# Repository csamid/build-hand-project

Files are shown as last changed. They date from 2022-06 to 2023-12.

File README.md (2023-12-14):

# CSULB BUILD Hand Project

As an CSULB NIH BUILD Scholar I worked in the Robotics and Interactive Systems Engineering laboratory on a hand rehabilitation project. This project was co-advised by Dr. Panadda Marayong and Dr. I-Hung Khoo (many thanks to them!). The goal of our project was to measure hand forces and torques for evaluation and rehabilitative training of individuals with hand impairment. Our project consists of a knob device and a grip-load device to simulate interactions that involve power and precision. Below you can find more details on each device and some other work I did.

> [!NOTE]
> This repo is primary for future csulb students that will build ontop of the work I and many previous students developed. However anyone can view/use the material. Feel free to contact me if you have any questions!

## Contents
- [Grip Load Device](#grip-load-device)
- [Brace](#bracee)
- [Knob Device](#knob-device)
- [Hapkit](#hapkit)

## GRIP LOAD DEVICE
The Grip-Load Device (GLD) runs on a Arduino Uno and incorporates data from three sensors:
- MPU6050 for acceleration to measure load force during dynamic tests. 
- LCFD-50 load cell to capture grip force 
- LSB302 Futek load cell to assess load force during static tests

The purpose of this device is to assess the differences in grip-load force coordination between healthy and hand impaired individuals. We also hope this device can provide rehabilitative training to individuals with hand impairment.

Dive deeper into the Grip Load Device:

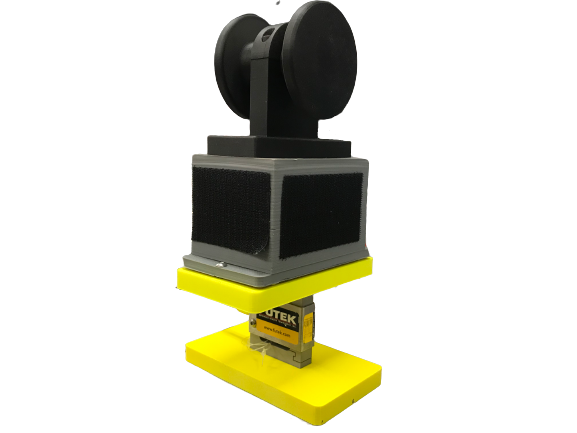
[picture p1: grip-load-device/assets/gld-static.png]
gld device


# Brace
A 2 piece 3d printed adjustable brace to explore the effects of wrist position on grip-load force coordination. It can be set at -30, 0, and 30 degrees at the wrist.

Head to the Brace directory: 

<div style="text-align: center; padding-bottom: 50px;">
<a href="brace/">
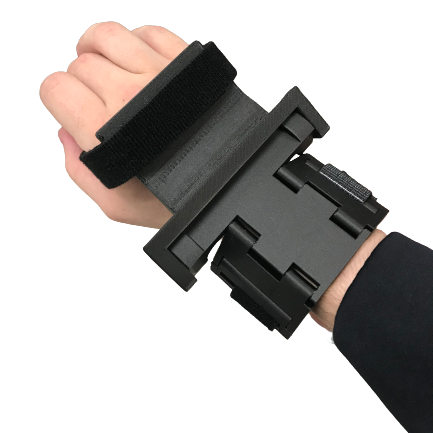
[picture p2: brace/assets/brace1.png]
brace
  
</a>
</div>

# Knob Device
The knob device centers around an Arduino Uno, sending data to a  graphical user interface (GUI) and controlling a haptic interface. This device aims to assess the coordination between grasping force and  turning torque. LabVIEW  handles the GUI and data acquisition. The haptic interface comprises a HEDS encoder, a maxon A-max motor, force sensing resistors  (FSR), and a torque sensor.

Dive deeper into the Knob Device:

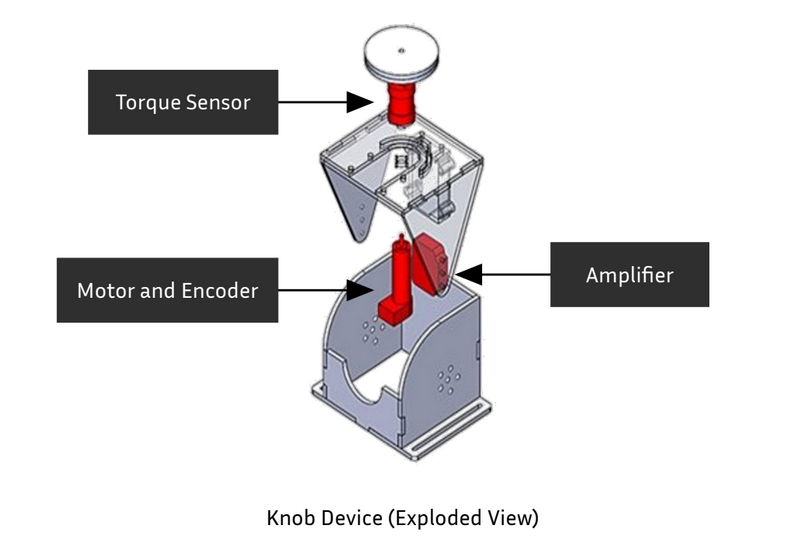
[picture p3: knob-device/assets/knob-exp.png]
Knob Device


# Hapkit
Some design changes were made to the open-source Hapkit 10.01.14 from Stanford to fit with available hardware at the RISE Lab @CSULB.

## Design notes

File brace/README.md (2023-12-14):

## Brace

Project Timeline: Feburary 2022 - May 2022

### Contents
- SolidWorks Files
- 3D printer Files
- References
- Bill of Materials

### Bill of Materials
| Category          | Product                  | Description          | Individual Quantity per Brace | Purchase Quantity | Price  |
| ----------------- | ------------------------ | -------------------- | ------------------------------ | ----------------- | ------ |
| Hardware          |                          |                      |                              |                   |       |
|                  | [Heat Threaded Inserts](https://www.mcmaster.com/94180a331/) | M3, 3.9 mm length         | 2                            | 1                  | $16.81 |
|                  | [Heat Threaded Inserts](https://www.mcmaster.com/94180A312/) | M2, 4.8 mm length         | 6                            | 1                  | $17.18 |
|                  | [Hex Socket Cap Screws](https://www.mcmaster.com/91292A833/)    | M2 10 mm length       | 6                            | 1                  | $7.91  |
|                  | [Socket Cap Screws](https://www.mcmaster.com/92855A310/)        | M3 10 mm length       | 2                            | 1                  | $2.50  |
| 3D Printed Parts  |                        |                      |                              |                   |       |
|                  | Palm (regular or large size)   | Printed in CSULB's Innovation Space (Markforged Printer, onyx material) | 1 | 1 | ~$5.00 |
|                  | Wrist (regular or large size)  | Printed in CSULB's Innovation Space (Markforged Printer, onyx material) | 1 | 1 | ~$5.00 |
| Other             |                        |                      |                              |                   |       |
|                  | [Velcro](https://www.amazon.com/gp/product/B00I0TTPL8/ref=ppx_yo_dt_b_search_asin_title?ie=UTF8&psc=1)                   | one-wrap strap 1"    | 1                            | 1                  | $6.50  |
| Total Cost        |                        |                      |                              |                   | $60.90 |

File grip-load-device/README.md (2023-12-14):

## Grip Load Device

Project Timeline (August 2021 - June 2022)

Check out my [presentation poster](assets/RSCA2022_Samid_Ceballos.pdf) to learn more!

#### For Students:
This repo contains the code, documentation, and parts for this device. The data collection is done on LabVIEW. Videos explaining how to download code, how arduino & LabVIEW code works, and how run the code can be found [here](https://www.youtube.com/playlist?list=PLc3eWZpUKAzyQBUwwpyzYRb3LxGoiJ5aO ).

### Bill of Materials
| Category    | Product                                       | Description                                    | Individual Quantity Needed |
| -----------  | -------------------------------------------- | ---------------------------------------------- | -------------------------- |
| Hardware    |                                              |                                                |                           |
|             | [Hex Socket Head Cap Screws](https://www.mcmaster.com/91251A346/)                    | 10-32, 7/8", Alloy Steel                      | 2                         |
|             | [Socket Head Screw](https://www.mcmaster.com/93615A380/)                             | 10-32, 1/2"                                  | 1                         |
|             | [Heat Threaded Inserts](https://www.mcmaster.com/93365A154/)                          | 10-32, 0.225"                                | 1                         |
| Electronics |                                              |                                                |                           |
|             | CSG110                                       | Strain gauge amplifier for the LSB302         | 1                         |
|             | LCFD-50                                      | Load Cell for Grip Force                      | 1                         |
|             | Futek LSB302                                 | Load Cell for Load Force                      | 1                         |
|             | MPU-6050                                    | 6-DOF Accl and Gyro sensor                    | 1                         |
|             | HX711                                       | Load Cell Amplifier                           | 1                         |
|             | Arduino Uno                                 | microcontroller                               | 1                         |
|             | PCB                                         | made in house by Dr. Khoo                    | 1                         |
| 3D Printed Parts |                                    |                                                |                           |
|                 | bottom_collar2                           | printed in CSULB's Innovation Space (Markforge Printer, onyx material)   | 1   |
|                 | plate_attachment                          | printed in CSULB's Innovation Space (Markforge Printer, onyx material)   | 2   |
|                 | top_collar2                              | printed in CSULB's Innovation Space (Markforge Printer, onyx material)   | 1   |
|                 | weightcomp                               | printed in CSULB's Innovation Space (Markforge Printer, onyx material)   | 1   |

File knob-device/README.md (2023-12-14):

## Knob Device

Project Timeline: June 2020 - May 2021

[Watch a presentation I gave to learn more!](https://www.youtube.com/watch?v=llJ-72yHejI)

#### For future students:
The code from this device has not been updated since mid 2021 so it can use some improvements. See the [Grip Load Device LabVIEW code](../grip-load-device/LabVIEW/) for improving the LabVIEW code. Improvements can be made on the arduino code to add/change the haptic environment (ex: Spring and Damper). Hardware/Sensor improvements are also welcome, since FSR's are not reliable quantitatively. 

My final work on this device was this 3D-printed snap lock for the torque sensor. This piece was never fully tested to support the torque we expect users to apply. Here would be a good place to start!

Snap Lock:

<a href="knob-device/">
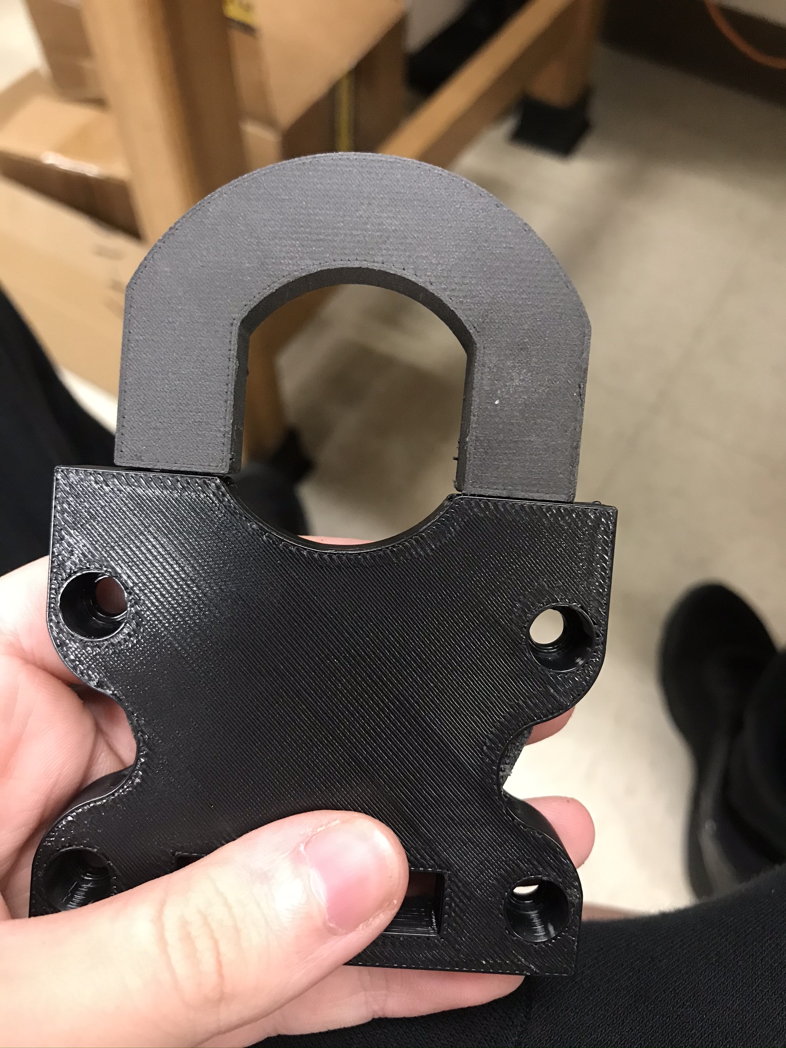
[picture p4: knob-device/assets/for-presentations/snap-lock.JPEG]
snap lock
  
</a>

Some notes on recorded max torque:

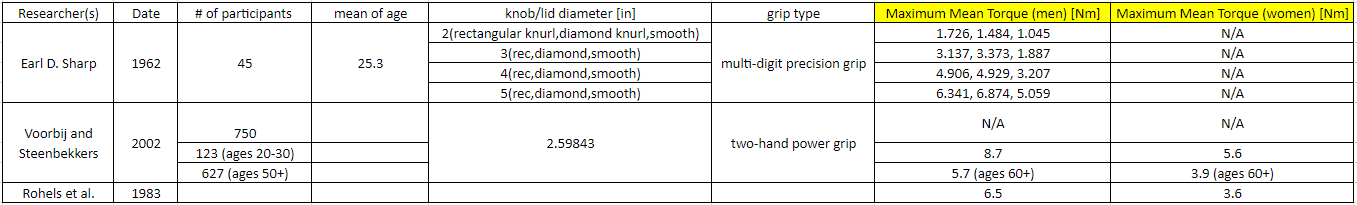
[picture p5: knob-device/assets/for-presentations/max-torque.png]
max-torque


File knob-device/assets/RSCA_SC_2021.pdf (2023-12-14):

# Hand Grasp Assessment Device with

# Variable Haptic Feedback– Work In

# Progress

# Samid Ceballos

1

, Panadda Marayong, Ph.D.
1

, and I-Hung Khoo, Ph.D.
2
[1] Department of Mechanical and Aerospace Engineering,

## [2] Department of Electrical Engineering

## Robotics and Interactive Systems Engineering (RISE) Laboratory

# Introduction

# Hand impairment is common in elderly over the age of 65 due

# to neuromuscular disorders and loss of skeletal muscle mass

[1]

# Previous robot-assistive devices can provide intensive hand

# rehabilitation which promotes neuroplasticity; however, these

# systems are costly[4,5]

# Previously, a low-cost device was developed to assess grip force

# vs load force and arm movement coordination

[3]

# Existing robot-assistive devices for turning tasks focus on

# turning torque[2,4] and grasping independently

[5,6]

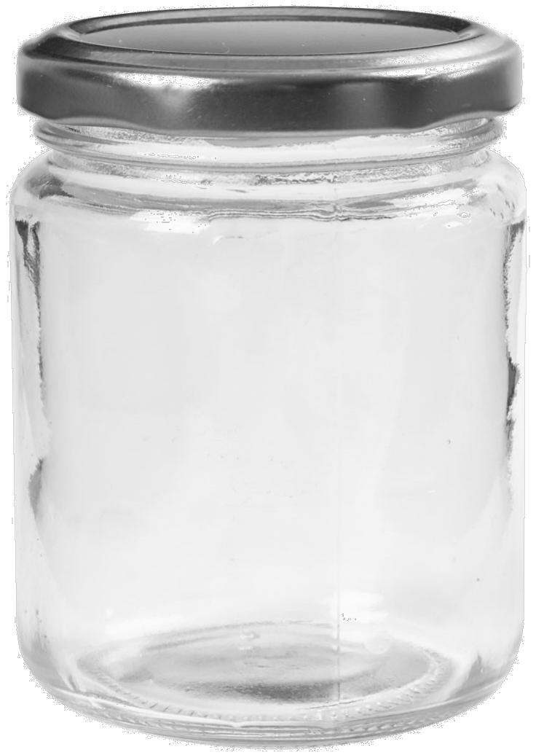
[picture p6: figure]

Figure 1. Jar

[7]

Hand Cup Body

Electronics
Chassis

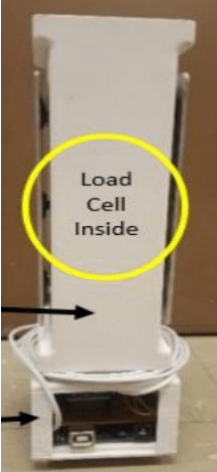
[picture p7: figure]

Figure 2. Grip/Load Device

# Acrylic structure with three available knob sizes

and five angles from the horizontal.

# DC motor with encoder for variable torque

# feedback and turn angle measurement

# Torque sensor to acquire turning torque

# Arduino Uno microcontroller with motor shield

# for sensor integration and actuation control

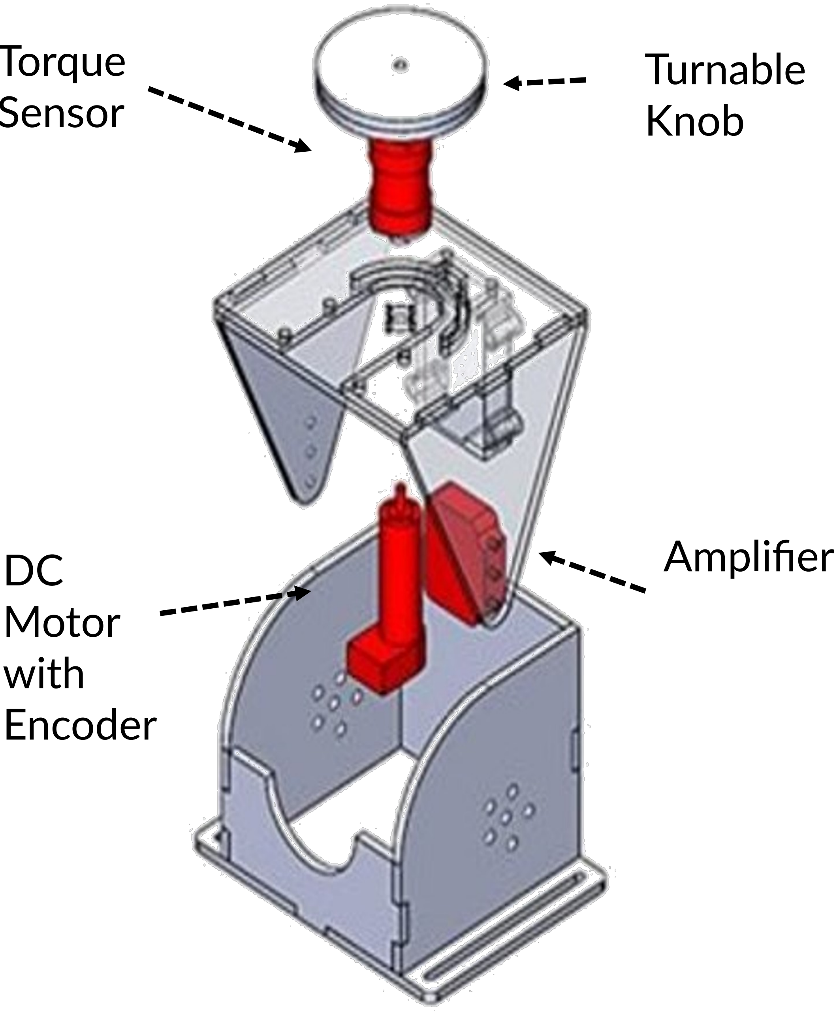
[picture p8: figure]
Amplifier; Motor; with; Encoder

Turnable
Knob

Torque
Sensor

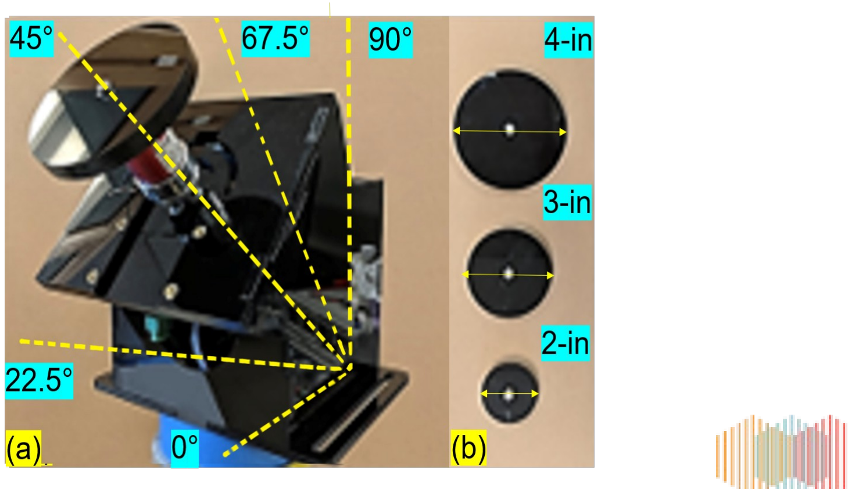
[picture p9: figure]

Figure 4. (a) Device at 45° plane from the horizontal (b) Available knob sizes

Figure 3. Exploded view

# Hand Device System Overview – Hardware Design

# Hand Device System Overview - Sensor Integration

# Force Sensing Resistor (FSR)

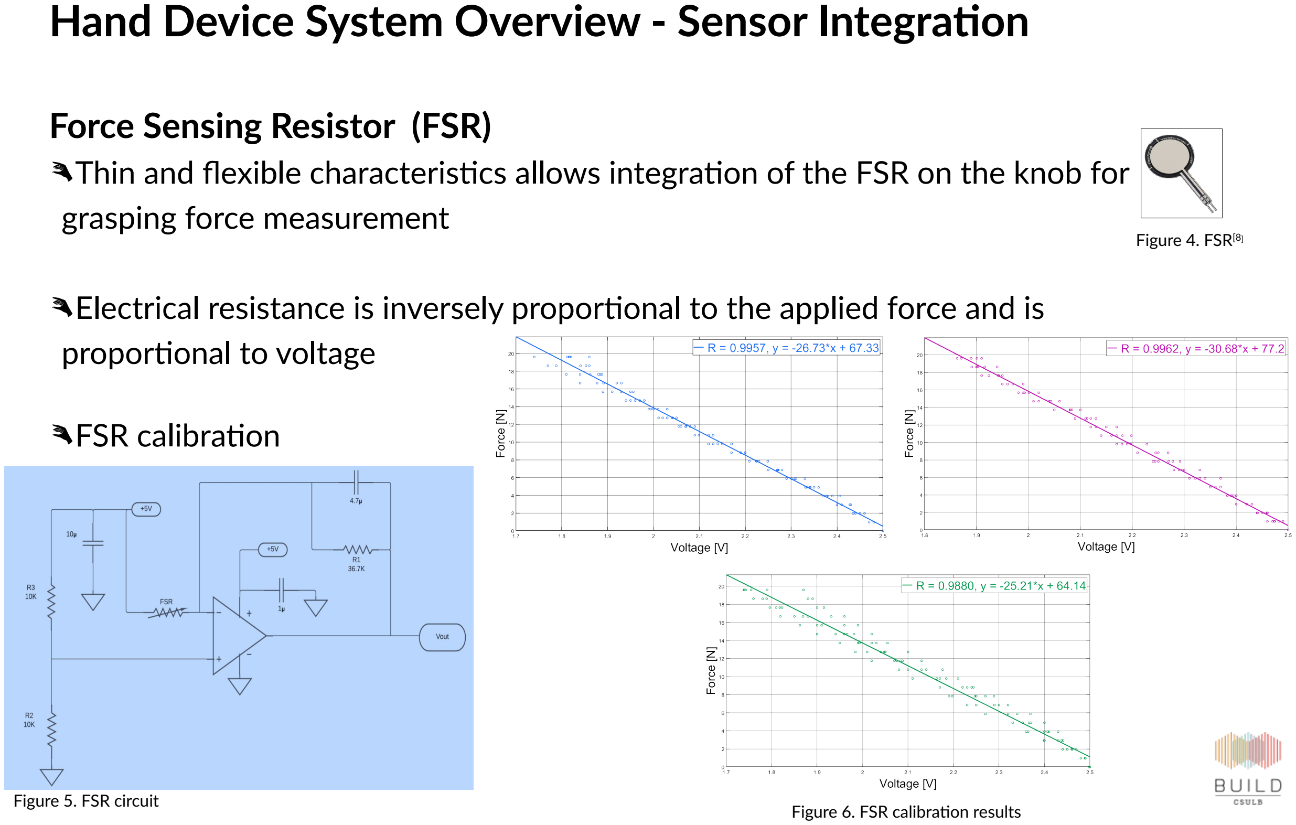
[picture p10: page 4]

# Thin and flexible characteristics allows integration of the FSR on the knob for

# grasping force measurement

# Electrical resistance is inversely proportional to the applied force and is

# proportional to voltage

# FSR calibration

Figure 4. FSR[8]

Figure 5. FSR circuit | Figure 6. FSR calibration results

# Hand Device System Overview - Sensor Integration

# Torque Sensor

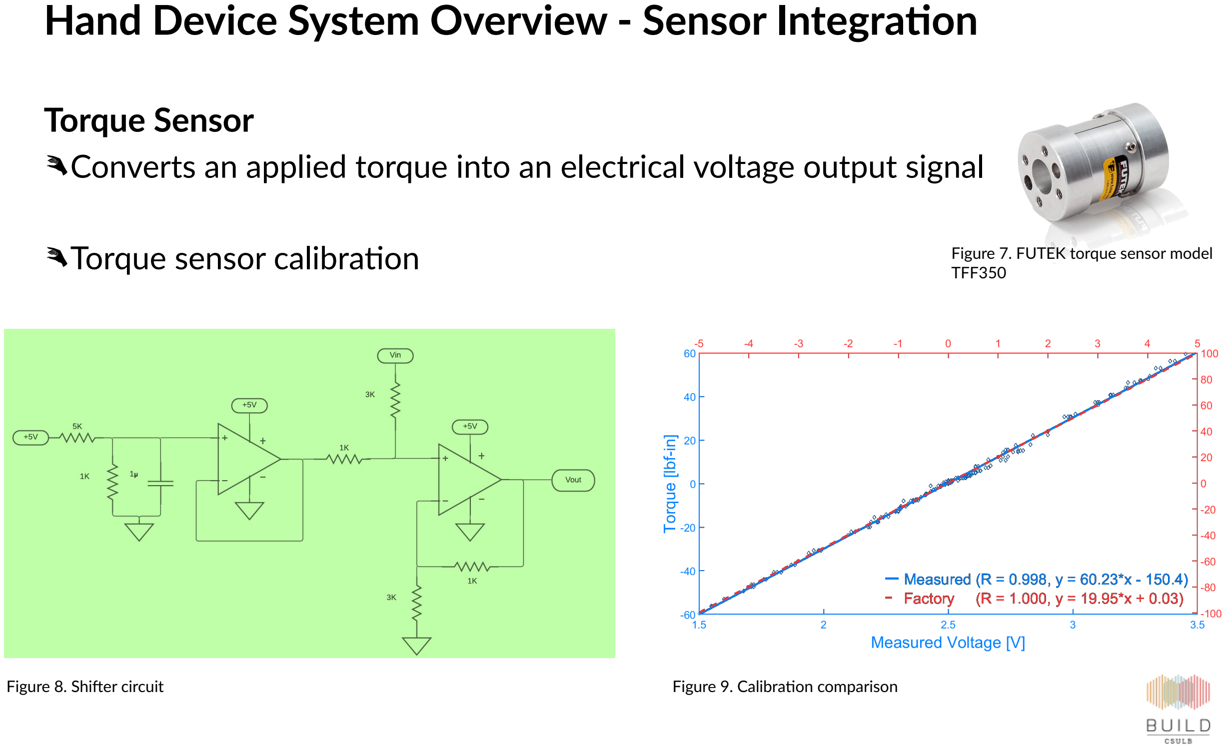
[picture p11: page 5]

# Converts an applied torque into an electrical voltage output signal

# Torque sensor calibration

Figure 8. Shifter circuit | Figure 9. Calibration comparison

Figure 7. FUTEK torque sensor model TFF350

# Hand Device System Overview –Graphical User Interface (GUI)

# Developed in LabVIEW to display experiment variables

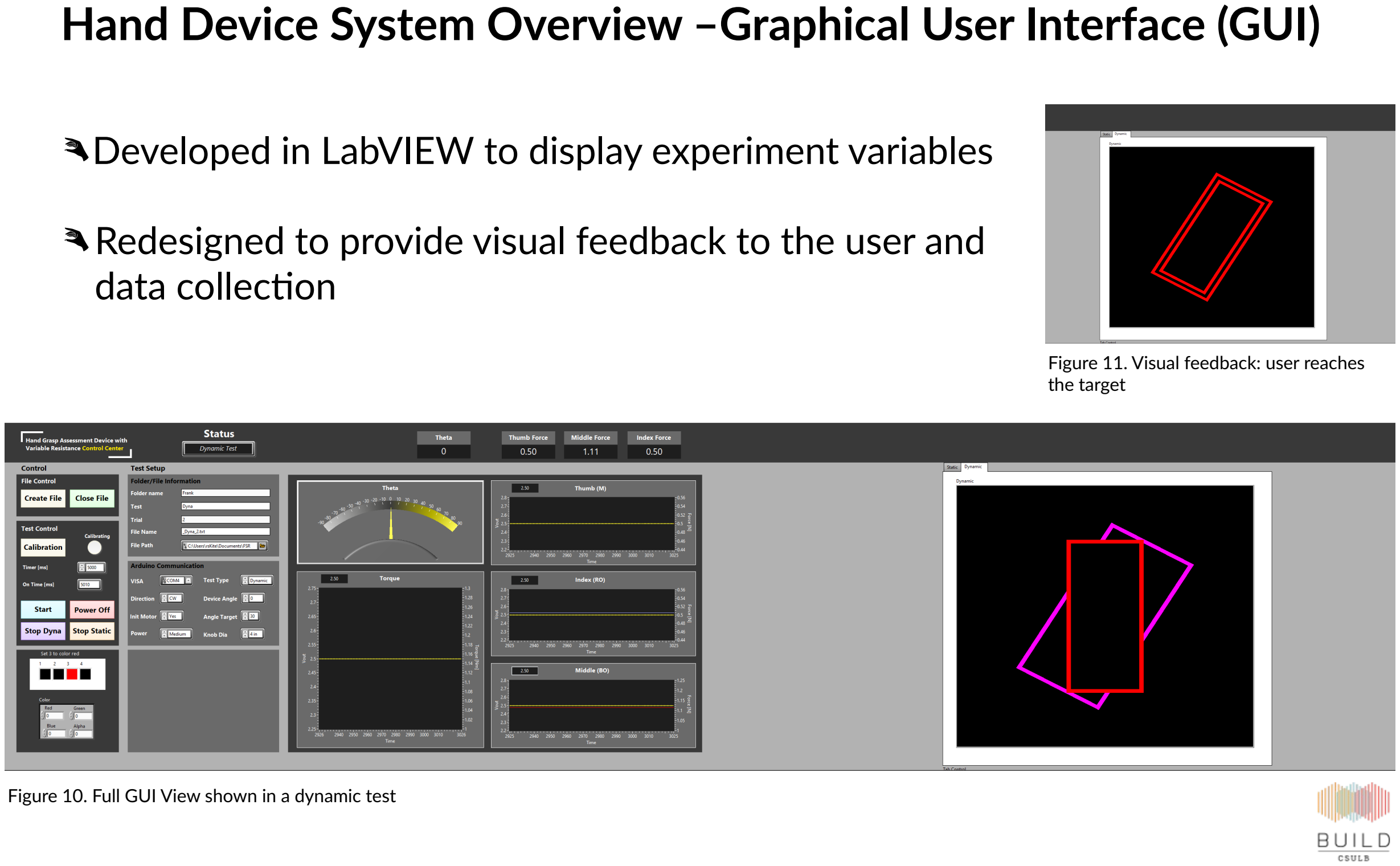
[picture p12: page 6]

Figure 10. Full GUI View shown in a dynamic test

Figure 11. Visual feedback: user reaches the target

# Redesigned to provide visual feedback to the user and

# data collection

# Hand Device System Overview

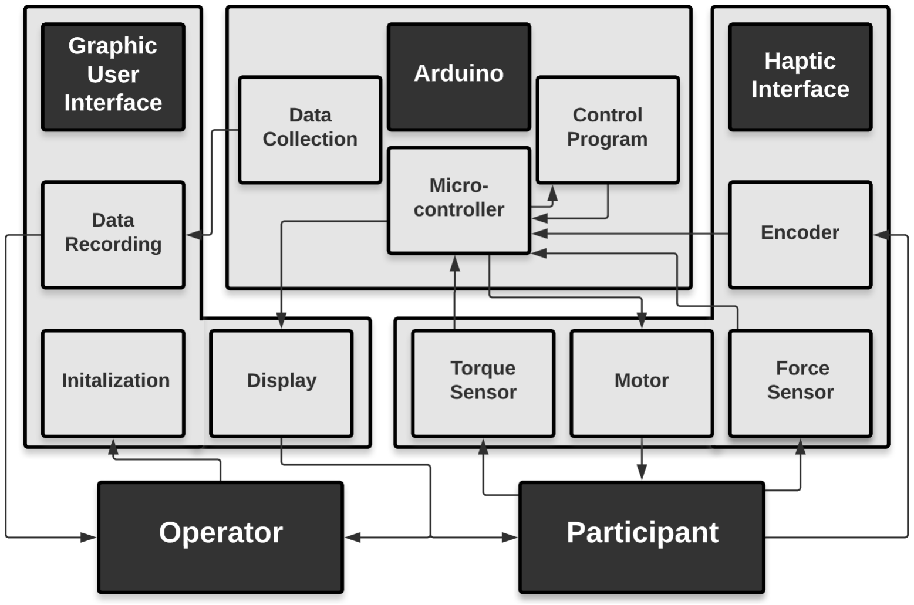
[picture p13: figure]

Figure 12. System design layout

# Human Subject Experiment Protocol

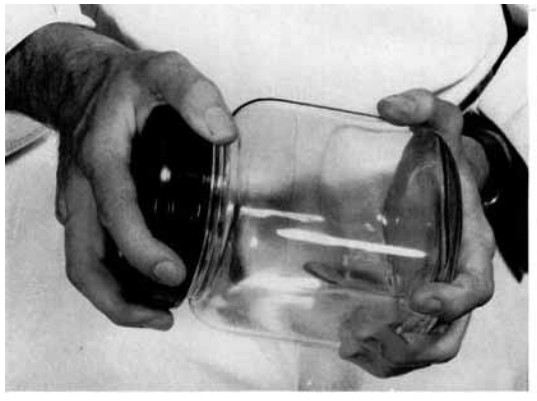
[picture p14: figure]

# Static Test (Power Focus)

# Max turning torque at varying knob sizes and wrist

# extension

# Dynamic Test (Precision Focus)

# Grasping force against turning torque at different

# resistance levels

# Target over- and undershoot of turn angle at varying

# torque feedback

# Time to target during target angle test

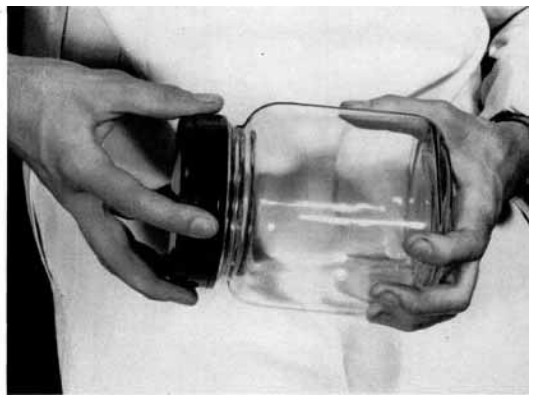
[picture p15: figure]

Figure 13. Transition of a power grasp (top) into a precision grasp (bottom) while opening a jar

[9]

# Future Work

# Redesign knobs for FSR integration and design attachment for static

# testing

# Test the functionality of the device with healthy subjects

# Baseline data collection for assessing coordination between

# grasping force and turning torque with healthy and hand impaired

# subjects

# Integration of a grip force/load force device that was previously

# developed for a more detailed hand evaluation

This research was supported by the National Institute of General Medical Sciences of the National Institutes of Health under Award Numbers; UL1GM118979; TL4GM118980; RL5GM118978. The content is solely the responsibility of the authors and does not necessarily represent the official views of the National Institutes of Health. The authors would like to thank Don G. Napasindayao for initial development of the device.

1.Carmeli, E., et al. “The Aging Hand.” The Journals of Gerontology: Series A, vol. 58, no. 2, 1 Feb. 2003, doi:10.1093/gerona/58.2.m146.

2.Gurari, N., and A. M. Okamura. “Human Performance in a Knob-Turning Task.” Second Joint EuroHaptics Conference and Symposium on Haptic

Interfaces for Virtual Environment and Teleoperator Systems (WHC'07), 2007, doi:10.1109/whc.2007.71

3.Herrera, D. "Hand Force and Arm Movement Coordination in Static and Dynamic Manipulation Tasks." California State University, Long Beach, 2018. [MS

Thesis]

4.Kazemi, H., et al. “A Robotic Interface to Train Grip Strength, Grip Coordination and Finger Extension Following Stroke.” 2012 Annual International Conference

of the IEEE Engineering in Medicine and Biology Society, 28 Aug. 2012, doi:10.1109/embc.2012.6346820.

5.Metzger, J., et al. “Design and Characterization of the ReHapticKnob, a Robot for Assessment and Therapy of Hand Function.” 2011

IEEE/RSJ International Conference on Intelligent Robots and Systems, 25 Sept. 2011, doi:10.1109/iros.2011.6094882.

6.Romeo, R.A, et al. "Development and preliminary testing of an instrumented object for force analysis during grasping," 2015 37th Annual Conference of the IEEE

Engineering in Medicine and Biology Society (EMBC), Milan, 2015, doi: 10.1109/EMBC.2015.7319935.

7.12 x Candle or Storage Jar. (n.d.). [Photograph]. Pastimes. https://www.google.com/url?sa=i&url=https%3A%2F%2Fwww.pastimesltd.co.uk%2F12-x-candle-or-

storage-jar-2698-p.asp&psig=AOvVaw3DwXC7F2fkro_Gv1-

1bnD1&ust=1615059864829000&source=images&cd=vfe&ved=0CAIQjRxqFwoTCODT4_30me8CFQAAAAAdAAAAABBW

8.FLEXIFORCE A401 SENSOR 25LBS. (n.d.). [Photograph]. Antratek Electronics. https://cdn.antratek.nl/media/product/8c2/flexiforce-a401-sensor-25lbs-sen-

11207-098.jpg

9.Napier, John R. "The prehensile movements of the human hand." The Journal of bone and joint surgery. British volume 38, no. 4 (1956): 902-913, doi:

10.1302/0301-620X.38B4.902.

# References & Acknowledgements

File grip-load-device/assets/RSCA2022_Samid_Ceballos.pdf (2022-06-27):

# A user interface for evaluating hand force coordination in static and dynamic

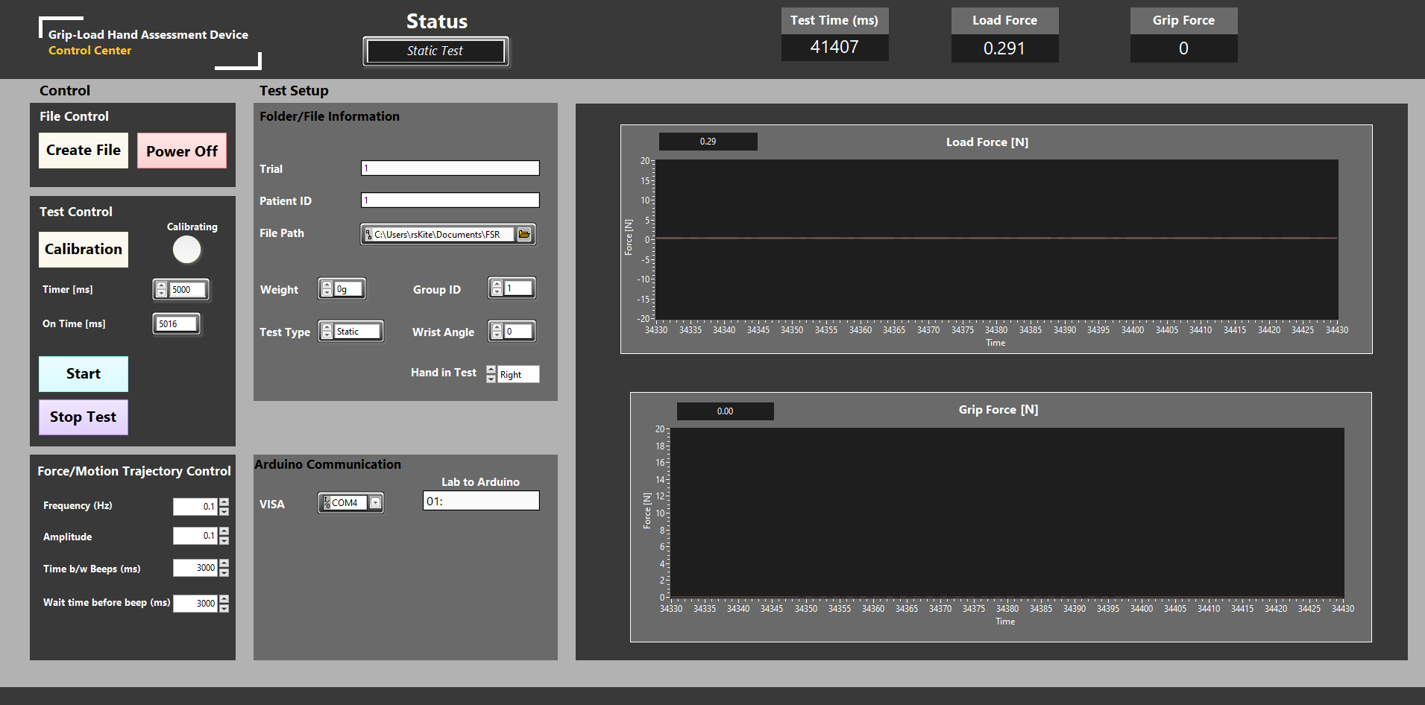
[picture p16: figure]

# manipulation tasks

## Samid Ceballos¹

## , Panadda Marayong, Ph.D.¹

, I-Hung Khoo, Ph.D.

2

## , and Vennila Krishnan, Ph.D., PT

3

## 1Department of Mechanical and Aerospace Engineering 2Department of Electrical Engineering 3Department of Physical Therapy

Haptic feedback

Visual feedback

Central Nervous System

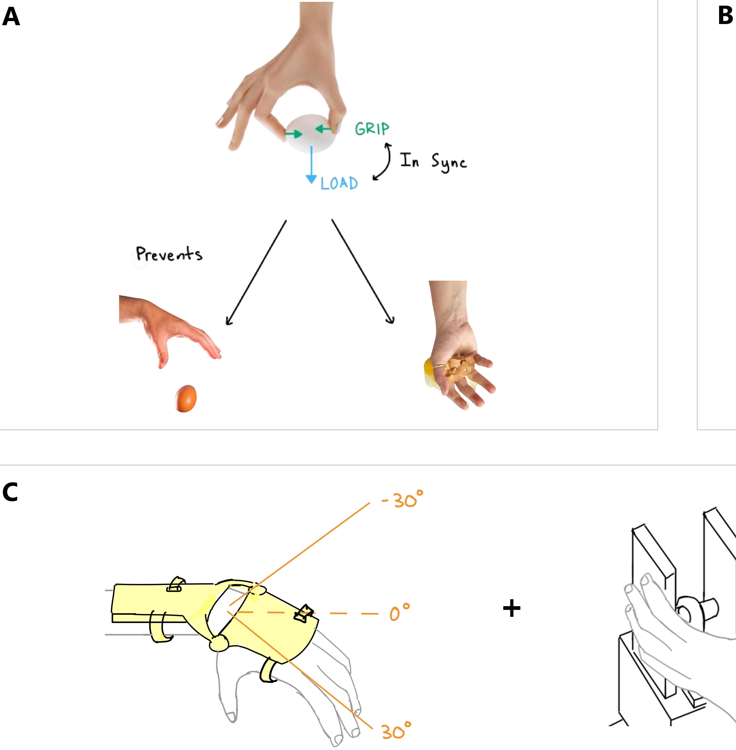
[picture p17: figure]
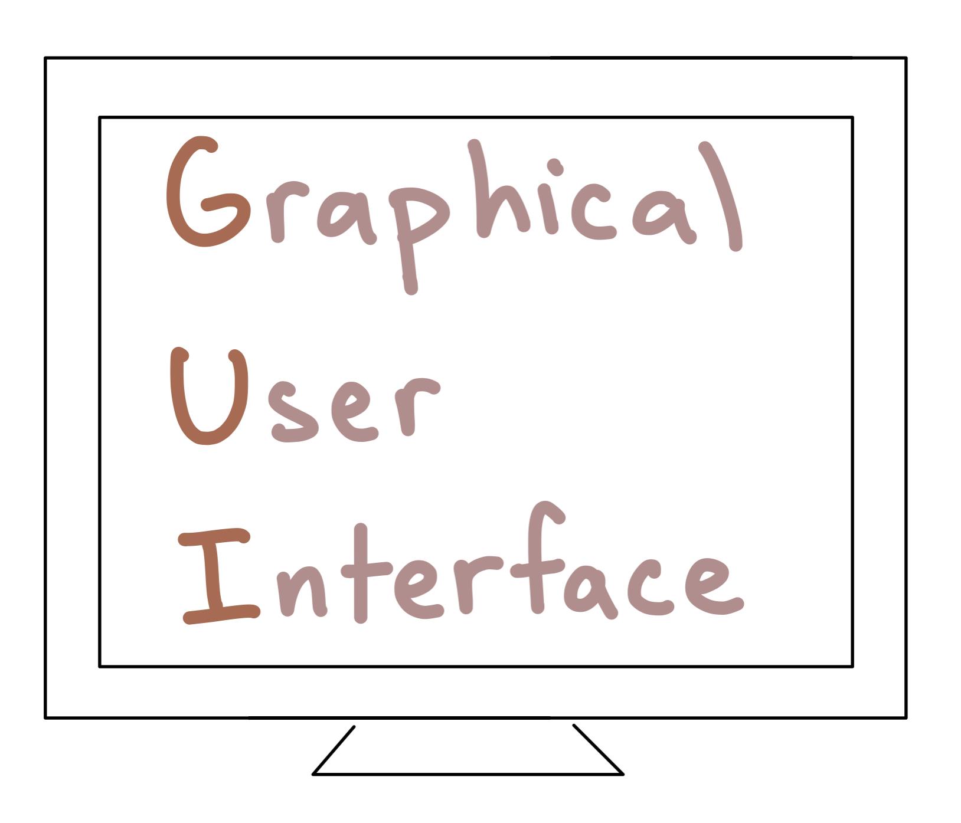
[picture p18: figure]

(A) A synchronous coordination of grip force (G; normal to the object contact area) and load force (L; tangential component) is needed to prevent object slippage or breakage (B) Visual and haptic feedback play a key role within the central nervous system to produce efficient manipulation (C) This work redesigns an interface which includes an adjustable brace to explore the effects of wrist position on grip-load force coordination, a device to measure grip and load, and a GUI for visual feedback.

## Introduction

- Hand impairment is common in elderly over the age of 65 due to neuromuscular disorders and loss of skeletal muscle mass

[1]

- Previously, a low-cost device was developed to assess grip force vs load force

[2]

- Post-stroke individuals suffer from hypertonicity
- Previous literature has investigated grip-load force coordination in static, dynamic, unidirectional, and bidirectional tasks, but

there exists a lack of research investigating the effect of wrist position on grip-load force coordination while a user receives

visual feedback [3,4,5]

## Objective

Redesign a hand assessment interface to:
- improve force measurement accuracy
- provide visual feedback to the user
- design an adjustable wrist brace to investigate the effect of

wrist angle on grip-load force coordination

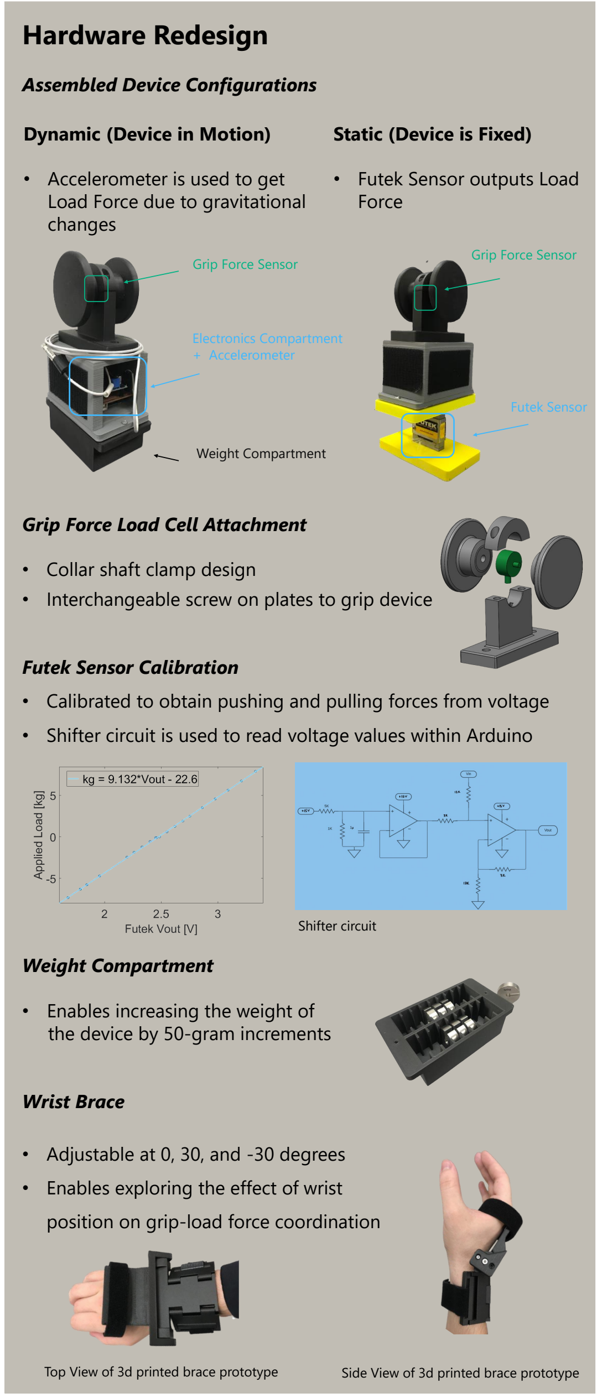
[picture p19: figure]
Hardware Redesign; Assembled Device Configurations; Grip Force Load Cell Attachment; • Collar shaft clamp design; Futek Sensor Calibration; Weight Compartment; • Enables increasing the weight of the device by 50-gram increments; Wrist Brace; • Adjustable at 0, 30, and -30 degrees; • Enables exploring the effect of wrist; position on grip-load force coordination; Shifter circuit; Static (Device is Fixed); • Futek Sensor outputs Load Force; Dynamic (Device in Motion); • Accelerometer is used to get Load Force due to gravitational changes; Electronics Compartment + Accelerometer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

- Interchangeable screw on plates to grip device
- Calibrated to obtain pushing and pulling forces from voltage
- Shifter circuit is used to read voltage values within Arduino

## Software Redesign

- GUI redesigned in LabVIEW
- Allows for data collection with Arduino microcontroller
- Enables the implementation of visual feedback

## Planned User Study & Ongoing Work

Dynamic Test

- Evaluating grip-load force coordination
- User performs a lift-hold-lower

task based on a metronome

- Weight of device is increased
- Brace is used at the 3 positions

Static Test

- Evaluating grip-load force coordination in unidirectional and

bidirectional tasks and at 3 wrist positions

- User performs a pull and push task based on a metronome
- User tracks a ramp force trajectory by pulling on the device

Ongoing Work

- Integrating the visual feedback in LabVIEW
- Redesigning a circuit board to include shifter circuit
- Finalizing the wrist brace design

Grip-Load Device

## References & Acknowledgements

1. Carmeli, E., et al. “The Aging Hand.” The Journals of Gerontology: Series A, vol. 58, no. 2, 1 Feb. 2003, doi:10.1093/gerona/58.2.m146.
2. Herrera, D. "Hand Force and Arm Movement Coordination in Static and Dynamic Manipulation Tasks." California State University, Long Beach, 2018. [MS Thesis]
3. de Freitas PB, Markovic G, Krishnan V, Jaric S. Force coordination in static manipulation: discerning the contribution of muscle synergies and cutaneous afferents. Neurosci Lett. 2008 Mar 28;434(2):234-9. doi: 10.1016/j.neulet.2008.01.067. Epub 2008 Feb 6. PMID: 18313221; PMCID: PMC2323603.
4. de Freitas, Paulo B., Vennila Krishnan, and Slobodan Jaric. "Force coordination in object manipulation." Journal of Human Kinetics 20.1 (2008): 37-50.
5. Toma, Simone, Veronica Caputo, and Marco Santello. "Visual feedback of object motion direction influences the timing of grip force modulation during object manipulation." Frontiers in human neuroscience 14 (2020): 198.

This research was supported by the National Institute of General Medical Sciences of the National Institutes of Health under Award
Numbers; UL1GM118979; TL4GM118980; RL5GM118978. The content is solely the responsibility of the authors and does not necessarily represent the official views of the National Institutes of Health. The authors would like to thank Daniela Herrera and Ambarish Nayak for initial development of the
device. Top View of 3d printed brace prototype | Side View of 3d printed brace prototype

Operator view of the GUI

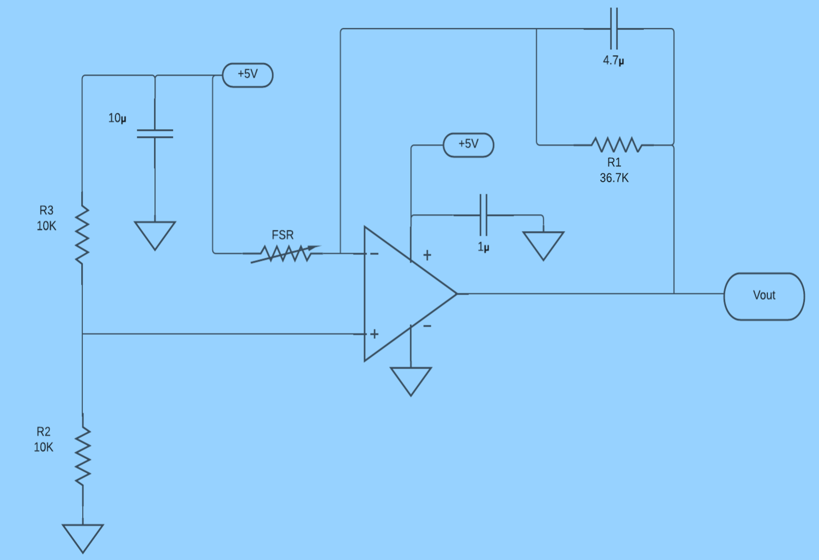
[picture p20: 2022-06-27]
knob-device/assets/important/fsr-circuit.png

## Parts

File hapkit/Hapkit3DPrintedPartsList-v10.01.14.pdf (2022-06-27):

## Hapkit (3D Printed) Parts List

version 10.01.14

In order to make your Hapkit, you will need to gather (or make) all the parts shown in the table below and (as a group) in the picture at right.

The total cost of the Hapkit will likely range in price from $50 to $100, depending on where you get the parts, shipping costs, and what resources you have at hand. We provide online resources for purchasing most parts, although in many cases you can substitute with parts found at your local hardware store. (Many parts purchased online can only be found in bulk, but you may be able to buy parts individually at a local store.) If you are new to building mechatronic devices, we suggest that
you purchase the specifically recommended items as much as possible.

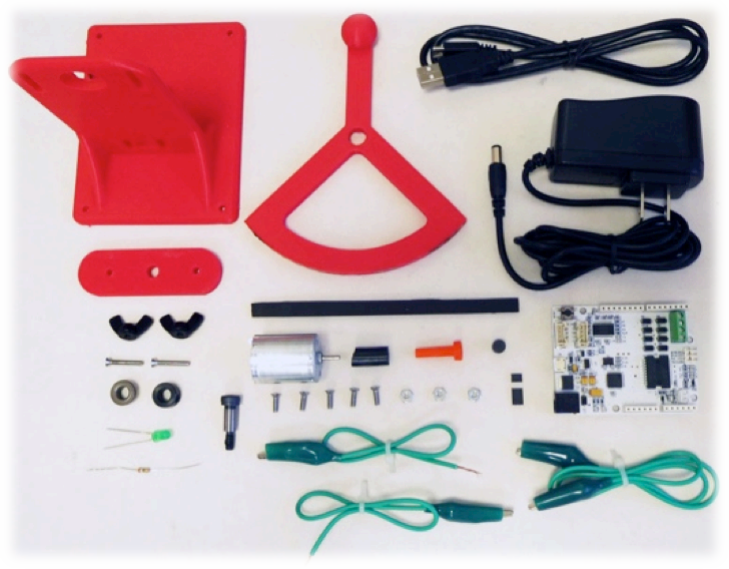
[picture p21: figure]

Component | (not to scale) Photo | Quantity | How to get this part | Approximate cost per Hapkit

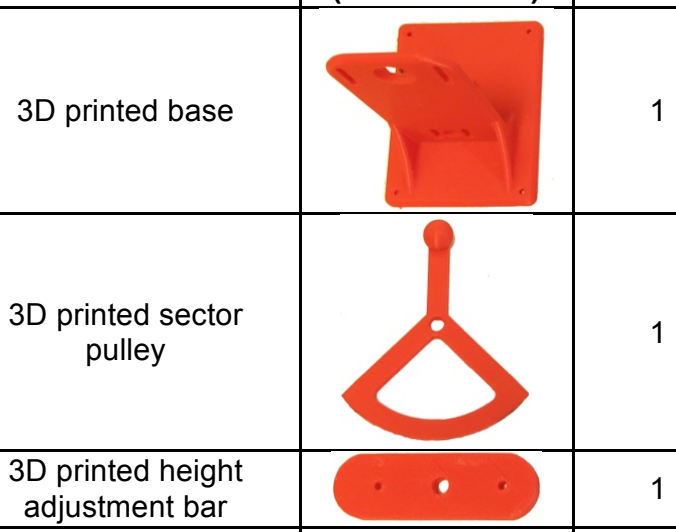
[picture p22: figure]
3D printed sector pulley; 3D printed height adjustment bar

3D printed base | | 1 | These parts are 3D printed using the files available at http://hapkit.stanford.edu/build.html. See the 3D printing tips in the Assembly document for more information. We have successfully built these parts using several commercially available consumer-type 3D printers, including the Makerbot Replicator 2, Printrbot, and Up. | Cost of PLA (thermoplastic used in the Makerbot) to print all these parts is approximately $10. The total weight of plastic used is about 100 grams. If you don't have direct access to a 3D printer, see the 3D printing tips document on the Hapkit website.
3D printed drive wheel/magnet holder | | 1
Wingnuts (for height adjustment) size 4-40 (size 4 bolt with 40 threads per inch) | | 2 | McMaster-Carr (http://www.mcmaster.com) sells in packs of 100: part number 98143A005 | $12.29 per pack of 100 ($0.24 for two), not including shipping
Screws (for height adjustment) size 4-40, at least 3/4" length | | 2 | McMaster-Carr (http://www.mcmaster.com) sells in packs of 100: part number 91781A113 | $4.75 per pack of 100 ($0.10 for two), not including shipping
Neoprene strip with thickness 1/8", width 1/4", and length approximately 6", ideally with adhesive backing. | | 1 | McMaster-Carr (http://www.mcmaster.com) smallest size available is a 6"x6" sheet that can be cut into smaller pieces with a knife: part number 8463K22 to 8463K42 | $9.79 for a 6"x6" piece with adhesive backing (about $0.50 per strip), not including shipping
Neoprene tubing, 3/16" inner diameter, 3/8" outer diameter, cut to 3/4" length | | 1 | We purchased a very long tube from Small Parts via Amazon (http://www.amazon.com): part number B008BWPM8Y Note: You can adjust the size of your 3D printed parts to accommodate a different size neoprene tube. | $14.42 for a 50'-long tube ($0.22 per piece), not including shipping We have also found this at a local hardware store for $2.00 per foot.

Component | (not to scale) Photo | Quantity | How to get this part | Approximate cost per Hapkit
Bearing: SAE 863 bronze flanged-sleeve bearing for 1/4" shaft diameter, with 3/8" outer diameter, 1/4" length, and 1/2" flange outer diameter | | 1 | McMaster-Carr (http://www.mcmaster.com): part number 2938T1 | $0.49 for one bearing, not including shipping
Self-locking shoulder screw: alloy steel thread-locking shoulder screw, 1/4" diameter x 1/2" long shoulder, 10-24 thread | | 1 | McMaster-Carr (http://www.mcmaster.com): part number 91264A242 | $1.81 for one shoulder screw, not including shipping
Shaft collar: set screw shaft collar for 1/4" diameter rod, black-oxide steel | | 1 | McMaster-Carr (http://www.mcmaster.com): part number 9414T6 | $0.92 for one shaft collar, not including shipping
4-40 screws with length 3/8" for mounting motor and Hapkit board to 3D printed base (18-8 Stainless Steel Flat Head Slotted Machine Screw, 4-40 Thread, 3/8" Length) | | 5 (2 are for motor, 3 are for Hapkit board) | McMaster-Carr (http://www.mcmaster.com) sells in packs of 100: part number 91781A110 | $4.36 per pack of 100 ($0.22 for five), not including shipping
4-40 nuts for mounting Hapkit board to 3D printed base (Zinc-Plated Steel Machine Screw Hex Nut, 4-40 Thread Size, 1/4" Width, 3/32" Height) | | 3 | McMaster-Carr (http://www.mcmaster.com) sells in packs of 100: part number 90480A005 | $0.81 per pack of 100 ($0.03 for three), not including shipping
Motor: Mabuchi motor company, 12 Volt, 5600 RPM, shaft 0.78 diameter x 0.346 length (manufacturer's number RF370CA-15370) | | 1 | Jameco (http://www.jameco.com/): part number 238473 Note: This motor cannot necessarily be replaced with any 12-Volt DC motor; this particular motor was selected for its balance of cost and suitability for Hapkit (size; relatively low friction, inertia, and cogging torque; reasonably high torque constant and maximum continuous torque) | $3.49 for one motor, not including shipping
Magnet (Ultra-High-Temperature Alnico Disc Magnet, Grade 8, 1/4" Diameter, 1/4" Thick, 0.3 lbs. Maximum Pull) | | 1 | McMaster-Carr (http://www.mcmaster.com): part number 57295K73 | $1.87 for one magnet, not including shipping
Magnetoresistive sensor: NXP company, fully integrated single angular sensor, through-hole mounting type (manufacturer's number KMA210) | | 1 | DigiKey (http://digikey.com): part number 568-8399-1-ND Note: This sensor needs to be soldered to the Hapkit board as described in the assembly instructions . | $5.18 for one sensor, not including shipping

Component | (not to scale) Photo | Quantity | How to get this part | Approximate cost per Hapkit
Hapkit board: Custom printed circuit board similar to the Arduino, but with additional circuitry for reading the magnetoresistive sensor and power amplifier for driving the motor | | 1 | Seeed Studio (http://www.seeedstudio.com): part number KIT04300M Note: If you are very familiar with Ardiuno, sensor circuits, and motors, you can replace this board with an Arduino Uno and Ardumoto shield (with additional circuitry). However, the Hapkit board likely costs less than these items combined. | $35.00 for one board, not including shipping Note: As of this writing, Seeed is sold out of Hapkit boards. However, they are doing another manufacturing run, and the boards should be available in one week.

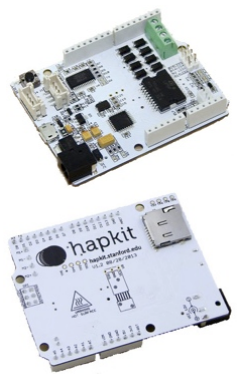
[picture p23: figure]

Power supply for Hapkit board: Should supply 12 V and 1 Amp. (Wall Power Adapter: 12VDC, 1A, 5.5×2.1mm Barrel Jack, Center-Positive) | | 1 | Pololu (http://www.pololu.com): part number 1466 Note: Similar items can be found from Digikey, Jameco, and other suppliers, but this is the least expensive one we have found. | $5.95 for one power supply, not including shipping
USB cable for communication between Hapkit board and computer: (3ft USB 2.0 A Male to Micro 5pin Male 28/28AWG Cable) | | 1 | Monoprice (http://www.monoprice.com): part number 4867 Note: Similar items can be found from other suppliers, but this is the least expensive one we have found. Also, we found that cables from some other sources did not fit as well into the female micro USB connector on the Hapkit board. | $2.40 for one USB cable, not including shipping
Leads with alligator clips on both ends (can cut one in half to make the two cables for motor power, also keep one intact for testing circuits) | | 2 | Mouser (http://www.mouser.com/): part number 835-501789 Note: These are available from many sources. You can also solder the leads to the motor instead of using alligator clips for a more permanent connection. If you solder, we suggest you use shrink tubing to protect the connection | $4.00 for a pack of 10 leads, not including shipping
Resistor (390 Ω) used for testing Hapkit board with LED | | 1 | Mouser (http://www.mouser.com/): part number 291-390-RC | $0.10 per resistor, not including shipping
Light-emitting diode (LED) used for testing Hapkit board | | 1 | Mouser (http://www.mouser.com/): part number 604-WP7113GD | $0.14 per LED, not including shipping

## Tools

You may also find it necessary to purchase (or gain access to) the following tools to create your Hapkit. Some of these tools may already be available in your house, school, or workshop – or can be borrowed from friends!

Tool | Photo (not to scale) | How to get this tool | Approximate cost
Superglue (we suggest gel-type single use packs; you will probably only need to use it once) | | Staples (http://www.staples.com): item 861702, model: AD119 This is available from many sources. | $2.25 for a package of four single-use tubes, not including shipping
Utility knife (or heavy duty precision knife) for cutting Neoprene pieces | | McMaster-Carr (http://www.mcmaster.com): part number 4927A11 part number 38995A71 | $5.22 for one utility knife, $4.41 for one precision knife, not including shipping
1/8" hex key (allen wrench) for shoulder screw | | McMaster-Carr (http://www.mcmaster.com): part number 7122A18 | $0.18 for one hex key, not including shipping
3/32" hex key (allen wrench) for shaft collar | | McMaster-Carr (http://www.mcmaster.com): part number 7122A16 | $0.17 for one hex key, not including shipping
Flathead screw driver for mounting screws (Miniature Metal-Handle Screwdriver, Nonmagnetic Precision Slotted Blade, 0.1" Wide Tip) | | McMaster-Carr (http://www.mcmaster.com): part number 7026A16 | $4.70 for one screw driver, not including shipping Note: If you can spend a little more money, a magnetized screwdriver can be very handy to prevent losing small screws
Soldering station (for connecting magnetoresistive sensor to Hapkit Board and/or motor leads to motor) | | Mouser (http://www.mouser.com/): part number 578-WES51 Soldering stations are available from a variety of sources at different costs. This one was selected for balance of performance and cost. | $130 for one soldering station, not including shipping You would also need to purchase solder.
Wire cutter/stripper (for cutting and stripping wires for electrical connections, particularly motor alligator clips) | | Jameco (http://www.jameco.com/): part number 127862 Wire cutter/stripper tools are available from a variety of sources at different costs. | $130 for one tool, not including shipping

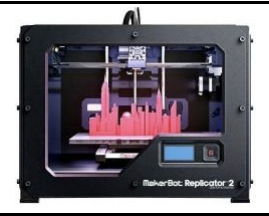
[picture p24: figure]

3D printer: We used a Makerbot Replicator 2 (4th generation) to make Hapkit parts | | Home Depot (http://www.homedepot.com): model number MP04948 Many other sources for this printer exist, and other types of 3D printers can be used as well. | $1,999* not including shipping

* You would also need to purchase a spool of PLA filament (thermoplastic material, comes in a variety of colors), which costs approximately $50 for a 2 lb. spool. (A spool this size should make about 9 Hapkits; smaller spools are available.) In addition, it is useful to have a scraper to help pry parts off the build platform tape, as well as replacement build platform tape.

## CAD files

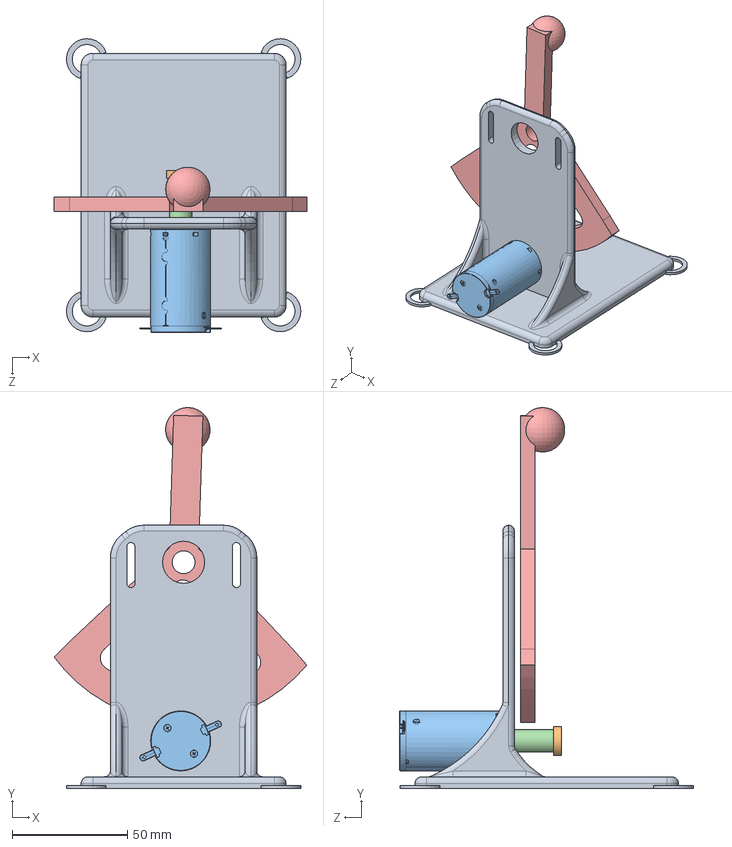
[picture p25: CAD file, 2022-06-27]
hapkit/Parts/CAD/HapkitAssem.SLDASM
109.5 x 165.1 x 127.2 mm
BaseV2
Drive_Wheel_V2
110923_Amax26_GB_6W_KL_1WE.stp
Sector_Pulley_V2

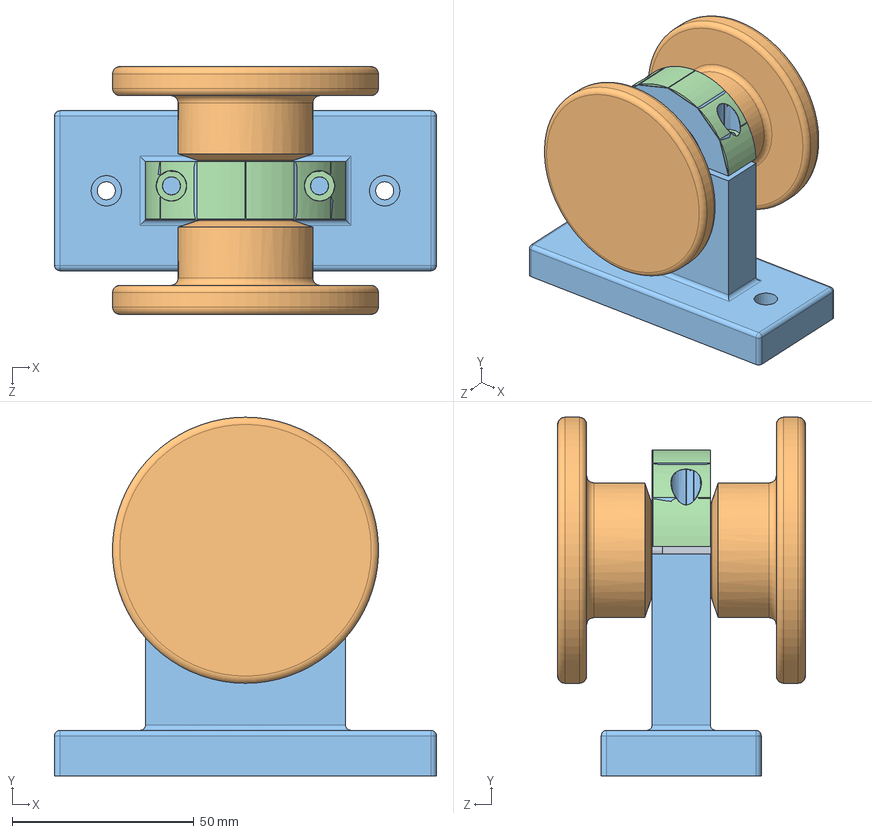
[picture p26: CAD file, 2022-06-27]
grip-load-device/SolidWorks/final-parts/FinalcollarAssembly.SLDASM
105.0 x 98.6 x 68.1 mm
LCFD
plate_attachment x 2
bottom_collar2
top_collar2

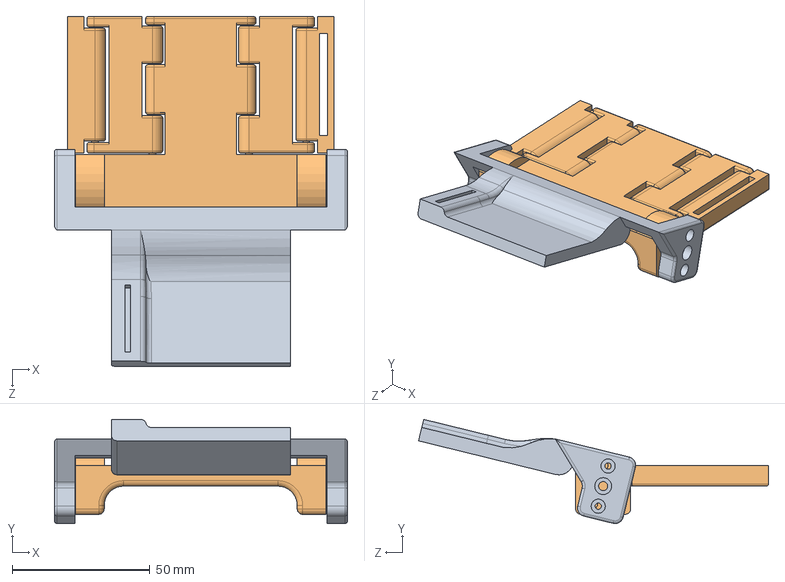
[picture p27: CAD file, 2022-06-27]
brace/SolidWorks/Brace.SLDASM
106.4 x 37.8 x 127.0 mm

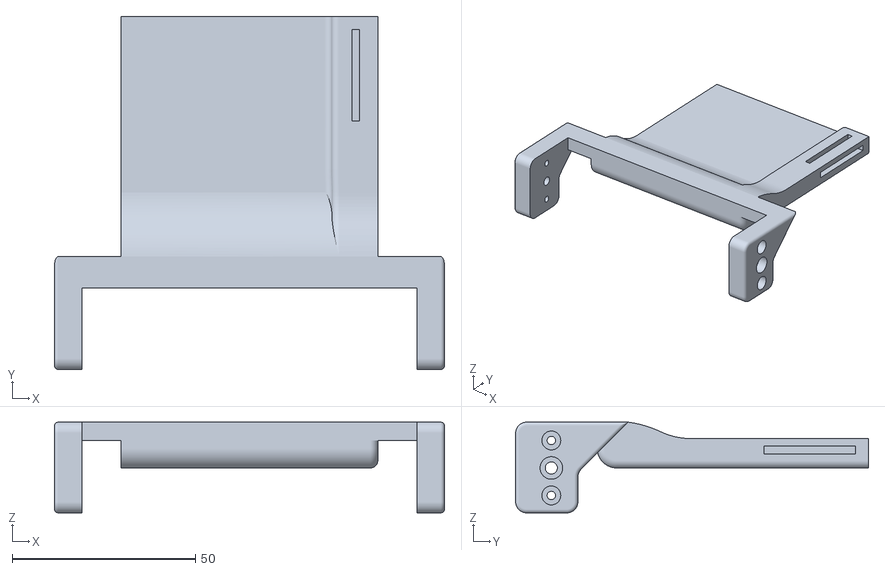
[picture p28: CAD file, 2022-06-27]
brace/3D-printer-files/Palm-large.STL
106.4 x 96.2 x 24.8

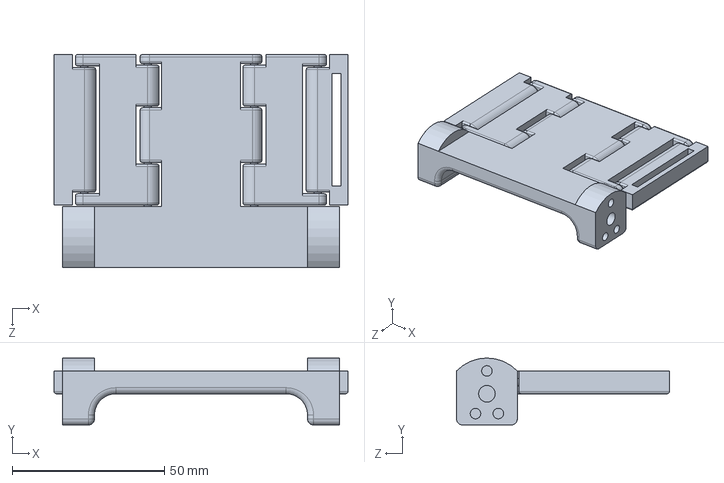
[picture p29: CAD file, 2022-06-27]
brace/SolidWorks/Wrist.SLDPRT
96.6 x 22.0 x 70.0 mm

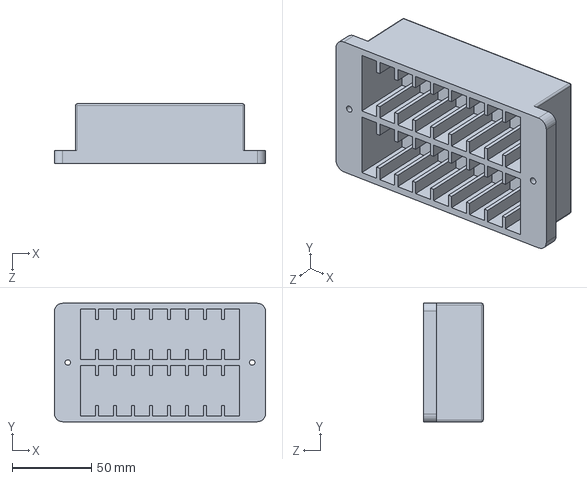
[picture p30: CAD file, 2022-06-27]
grip-load-device/SolidWorks/final-parts/weightcomp.SLDPRT
133.5 x 75.0 x 37.7 mm

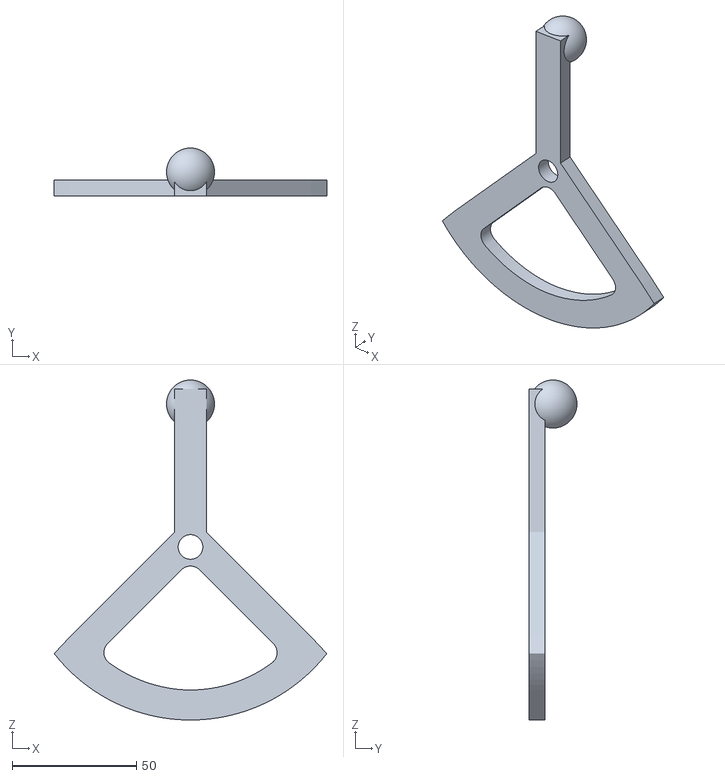
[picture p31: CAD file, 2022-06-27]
hapkit/Parts/3D-printer-files/SectorPulley.STL
109.5 x 19.3 x 136.6

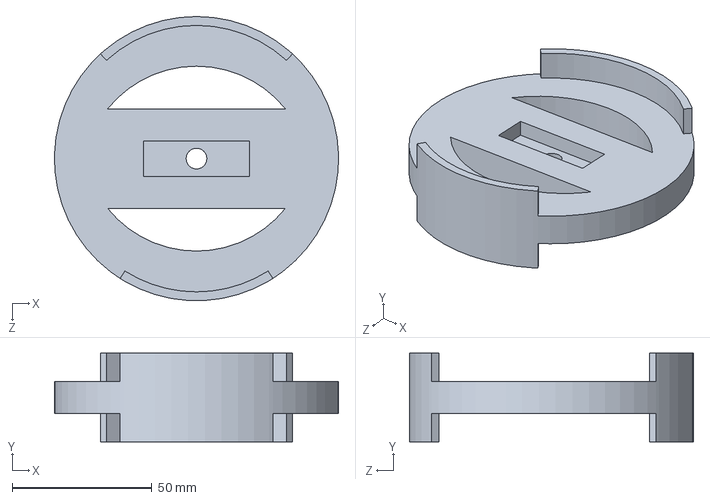
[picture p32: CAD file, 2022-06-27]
knob-device/SolidWorks/knob4.SLDPRT
101.6 x 31.8 x 101.5 mm

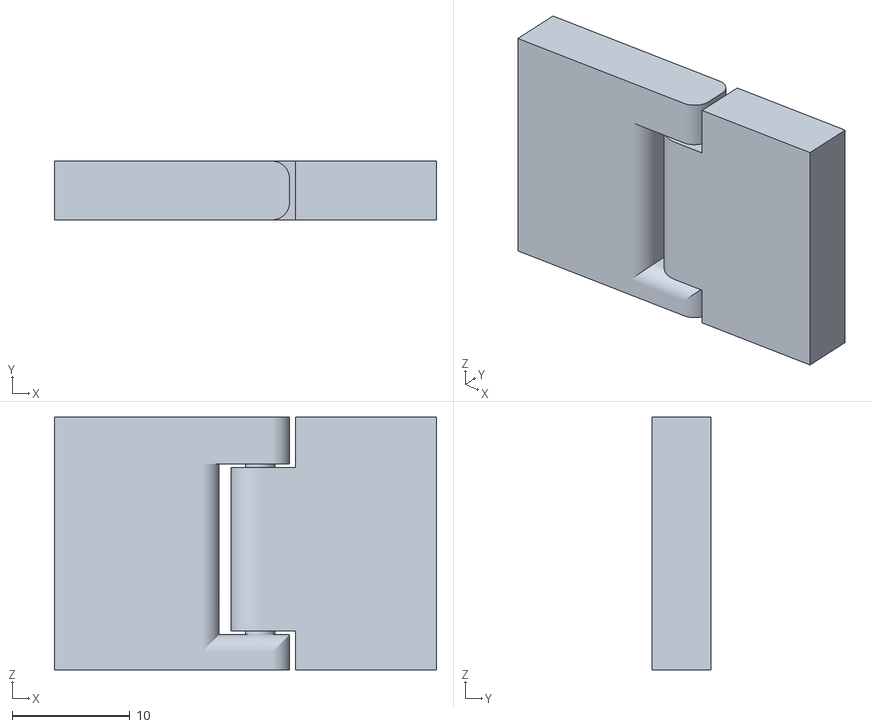
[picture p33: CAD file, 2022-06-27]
brace/3D-printer-files/hinge-test.STL
32.5 x 5.00 x 21.5

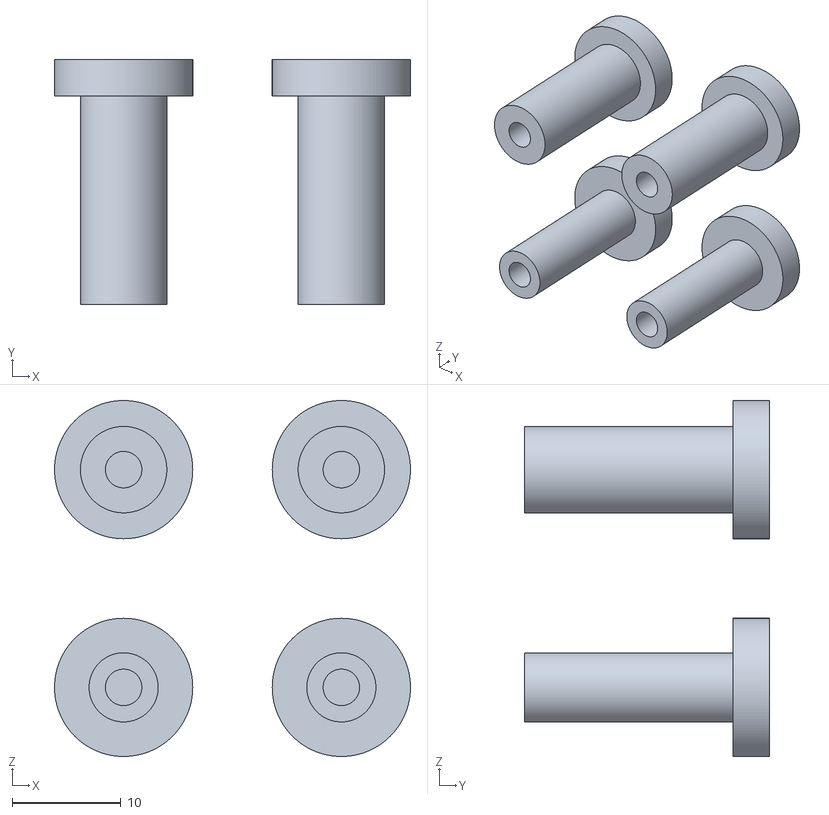
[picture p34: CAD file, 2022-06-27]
hapkit/Parts/3D-printer-files/DriveWheel_025x2_03125x2.STL
32.7 x 22.5 x 32.7

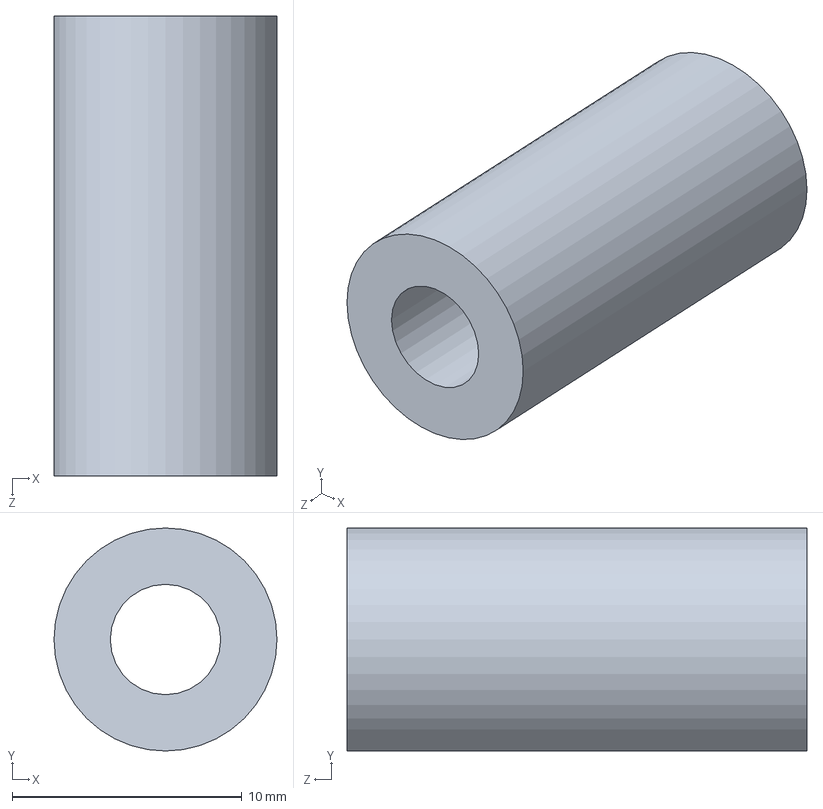
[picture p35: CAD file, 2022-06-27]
hapkit/Parts/CAD/neoprene.SLDPRT
9.70 x 9.70 x 20.0 mm

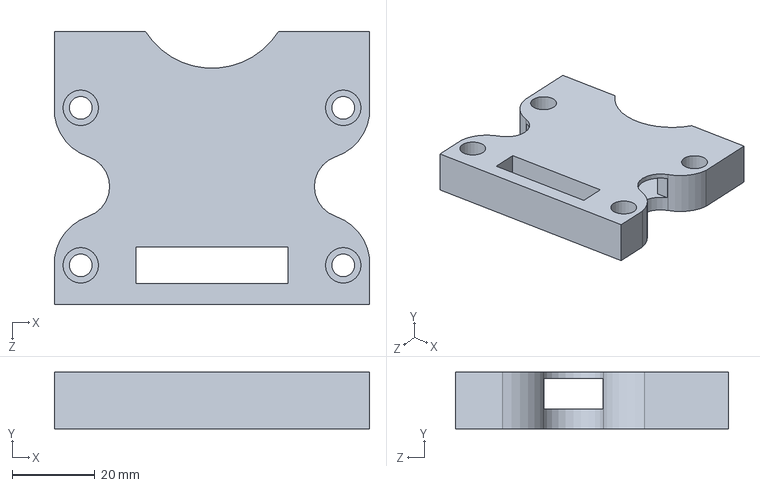
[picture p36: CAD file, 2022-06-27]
knob-device/SolidWorks/lock2bottom.SLDPRT
76.2 x 13.8 x 66.1 mm

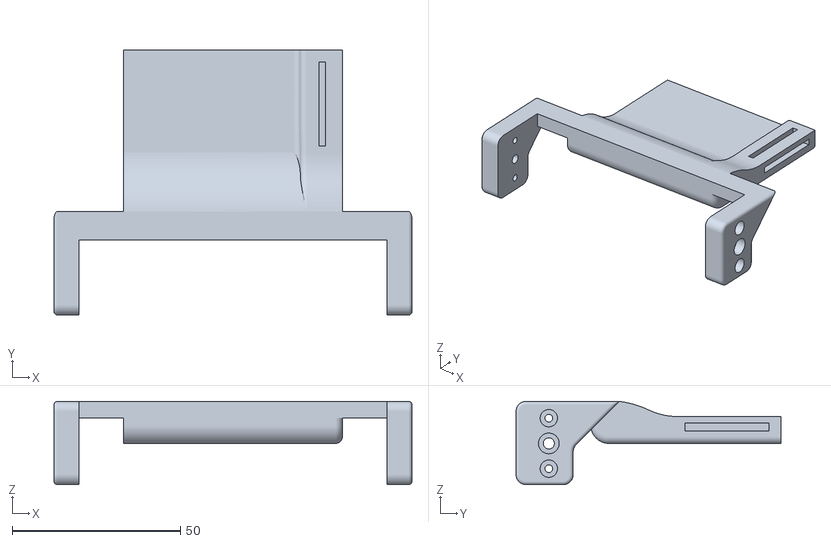
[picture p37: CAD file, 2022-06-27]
brace/3D-printer-files/Palm-regular.STL
106.4 x 78.8 x 24.8

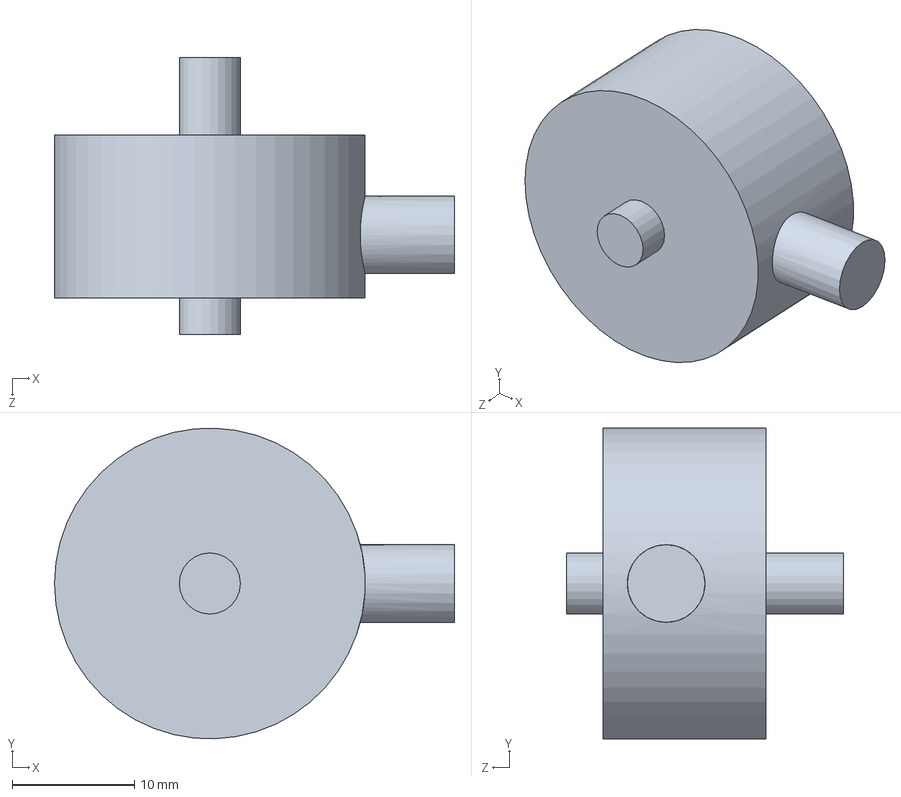
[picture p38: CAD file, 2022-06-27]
grip-load-device/SolidWorks/final-parts/LCFD.SLDPRT
32.7 x 25.4 x 22.6 mm

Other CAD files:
brace/SolidWorks/Palm.SLDPRT
hapkit/Parts/3D-printer-files/Base.STL
knob-device/SolidWorks/topsnap.SLDPRT
brace/SolidWorks/Hinge_test.SLDPRT
brace/SolidWorks/PalmLarge.SLDPRT
brace/SolidWorks/WristLarge.SLDPRT
brace/SolidWorks/spring_test.SLDPRT
grip-load-device/SolidWorks/final-parts/bottom_collar2.SLDPRT
grip-load-device/SolidWorks/final-parts/plate_attachment.SLDPRT
grip-load-device/SolidWorks/final-parts/top_collar2.SLDPRT
grip-load-device/SolidWorks/old-prototypes/Assem_Plates.SLDASM
grip-load-device/SolidWorks/old-prototypes/GFAttachmentOval.SLDPRT
grip-load-device/SolidWorks/old-prototypes/GFhexAttachment.SLDPRT
grip-load-device/SolidWorks/old-prototypes/LC_attachmentV2.SLDPRT
grip-load-device/SolidWorks/old-prototypes/LC_attachmentV3.SLDPRT
grip-load-device/SolidWorks/old-prototypes/R3_LC_attachment.SLDPRT
grip-load-device/SolidWorks/old-prototypes/R3_assembly.SLDASM
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

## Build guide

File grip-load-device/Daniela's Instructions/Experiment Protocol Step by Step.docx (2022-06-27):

Experimental Protocol

# Setup

1. Check the electronics. Make sure every wire is securely connected
2. If a static test will be ran, make sure to connect the battery wires
3. Attach goniometer on patient
4. Connect the Arduino to the computer
5. Open the virtual instrument (20200306_DynamicAndStatic_Final.vi) and make sure the correct Com port is selected for the Arduino. If using the same cable, it is COM4.

The rest of the procedures are with the assumption the set-up steps were followed.

# Dry Run

This is test is meant to verify the sensors capability to send serial data and have their values read by the virtual instrument. For this reason, you should run a dry run for each test (one for static and one from dynamic), since they each use different sensors.

# Static Test

Pretest:

- Change test configuration and setup
  - Mount device of vice with load cell holder
  - Make sure Futek load cell is connect
  - Make sure batteries are connected
- If not stated before, quickly summarize what the static test is about
  - Test left hand and right hand
  - No weights involved, since device is fixed
- Tell patient about the beeps
  - (1) Start of test. From resting position, go towards device and start pulling without stopping
  - (2) Stop pulling and return arm back to resting position
  - (3) Ignore. This is an extra beep for the dynamic test (might change)

Test:

1. Run the virtual instrument.
2. Modify the File Path (if necessary)
3. Calibrate the system
4. Select “Static Test” in the Test Case pull down
5. Select “0” in the Weight Applied pull down
6. Select “Right” or “Left” in the Hand in Test pull down
7. Enter a trial number
8. Enter the group ID
9. Enter the Patient ID
10. Start collecting data
11. Monitor data, make sure data seems reasonable. If not, investigate and restart
12. Stop collecting data
13. Ask patient if they need a break or would like to continue

# Dynamic Test

Beeps (0 – Not Started, 1 – Lift, 2 – Hold, 3 – Put Down)

Pretest:

- Change test configuration and setup
  - Attach empty weight compartment to device
  - Set aside weights
- If not stated before, quickly summarize what the static test is about
  - Test left hand and right hand
  - Test with no load and 450g
  - Device will not be fixed
- Tell patient about the beeps
  - (1) Start of test. From resting position, go towards device and start lifting. Aim for a 90 degree elbow position
  - (2) Hold device at 90 degrees
  - (3) Lower device back on table and return arm to resting position

Test:

1. Run the virtual instrument.
2. Modify the File Path (if necessary)
3. Calibrate the system
4. Select “Dynamic Test” in the Test Case pull down
5. Select “0” or “450” in the Weight Applied pull down
6. Select “Right” or “Left” in the Hand in Test pull down
7. Enter a trial number
8. Enter the group ID
9. Enter the Patient ID
10. Start collecting data
11. Monitor data, make sure data seems reasonable. If not, investigate and restart
12. Stop collecting data
13. Ask patient if they need a break or would like to continue

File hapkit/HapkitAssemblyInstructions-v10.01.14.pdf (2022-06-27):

### Hapkit (3D Printed) Assembly Instructions

version: 10.01.14

Note: These steps do not necessarily need to be performed in the order presented here. Except for a few components that are glued together, his version of Hapkit can be almost completely disassembled and reassembled.

1. Obtain the Hapkit components. Consult the parts list
provided, and purchase all the parts you don't already have on
hand. Figure out how you will access the necessary tools.
2. Use a 3D printer to create the four pieces colored red in the image at right: the base, the sector pulley, the height adjustment bar, and the drive wheel/magnet holder. The CAD files for these parts are available on the Hapkit website. Also
consult the 3D printing tips document on the Hapkit website for
useful suggestions and methods to customize your Hapkit.

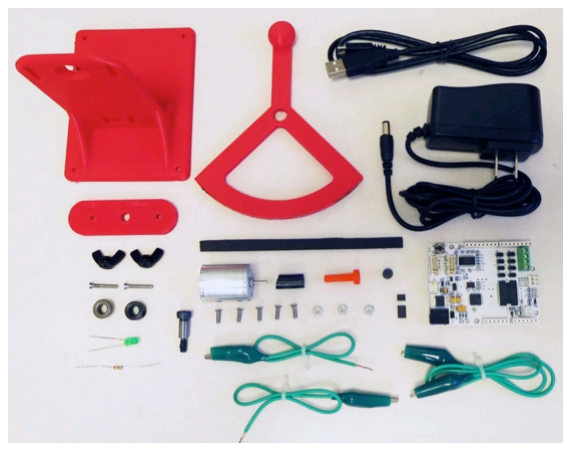
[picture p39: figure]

3. Assemble the motor and drive wheel. (a) Insert the 3D-printed drive wheel into the neoprene tube. If your drive wheel is loose within the neoprene, you can use superglue here. (This wasn't necessary for our 3D printed parts, but it may depend on the tolerance of your 3D printer and the neoprene you buy.) (b) Apply a small amount of superglue inside the drive wheel and then slip the drive wheel over the motor shaft. (c) Let dry for a few minutes. (d) Then place superglue into the magnet holder end of the 3D-printed drive wheel, and insert the magnet. (e) Let dry. When the motor shaft rotates, the cylinder-shaped magnet should rotate about an axis perpendicular to the cylindrical axis of the magnet.

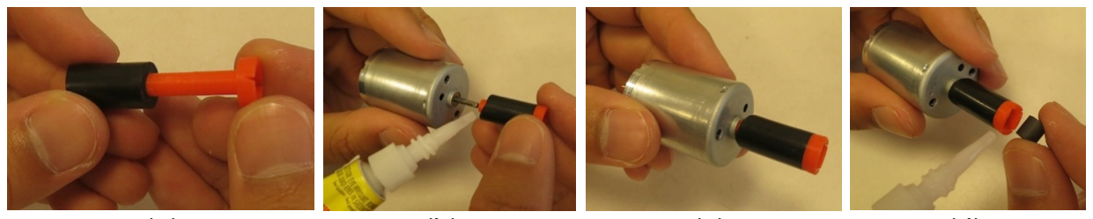
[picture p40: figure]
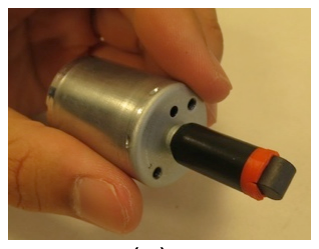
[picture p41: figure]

(a) | (b) | (c) | (d) | (e)
4. Attach the motor to the base. (a) Place the motor in the base by pushing the motor shaft through the hole as shown below. (b) Use two 4-40 screws with length 3/8" (not the longer screws!) in the slots on either side of the motor to secure the motor in place. The height of the motor/screws in the slots doesn't matter much; the slots just make it easier to place the screws. It is easiest to get the second screw in if you don’t tighten the first screw all the way. Once both screws have purchase, then tighten them. (c) Make sure the motor turns easily; the neoprene should not rub against the 3D printed base.

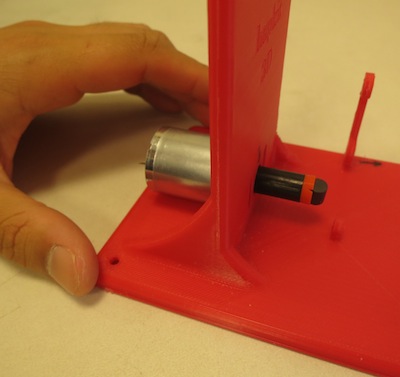
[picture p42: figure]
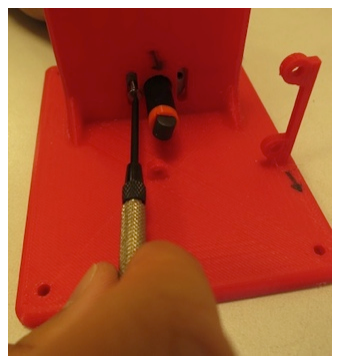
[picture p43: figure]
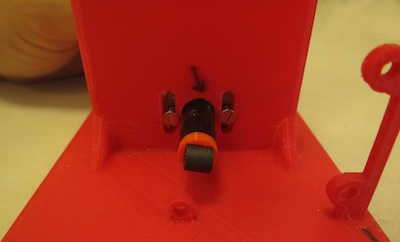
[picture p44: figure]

(a) | (b) | (c)
5. Assemble the sector pulley. (a) First, attach the neoprene strip to the sector pulley.
- If you have a neoprene strip with adhesive backing, remove the paper over the adhesive, and place the neoprene (sticky side up) on the table. Carefully attach the neoprene to the sector pulley by rolling the sector pulley along the neoprene, making it as smooth as possible. (If the ends of the neoprene strip do not stay fully attached, use a small drop of glue at the ends.)
- If your neoprene strip does not have adhesive backing, you will need to apply superglue to the beginning of the strip, then place the edge of the sector pulley on it and wait a little while for the glue. Then apply superglue to another section of the neoprene strip and roll the sector pulley over it. Repeat until the neoprene is securely attached to the entire bottom of the sector pulley.
(b) Cut off the remainder of the neoprene with a knife. (c) With the sector pulley laying flat on the table, insert the bearing into the hole. (d) Press it in so the flange makes solid contact with the sector pulley surface.

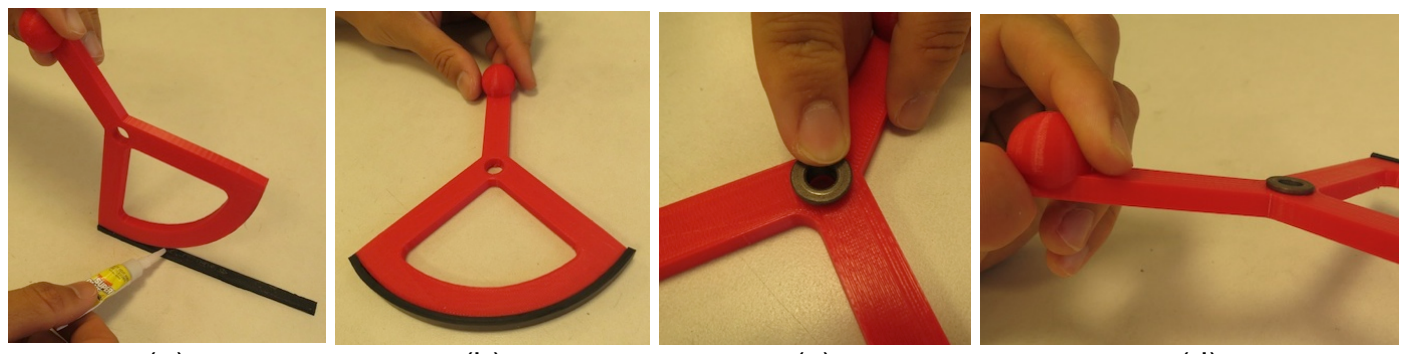
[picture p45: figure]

(a) | (b) | (c) | (d)
(e) Insert the shoulder screw into the bearing. (f) It should turn freely in the bearing. (g) Place the shaft collar over the shoulder screw and (h) use the 3/32" hex key (allen wrench) to securely attach the shaft collar to the bolt (not screw) part of the shoulder screw. (i) After assembly, you should be able to hold onto the screw part of the shoulder screw and freely swing the sector pulley around the bearing.

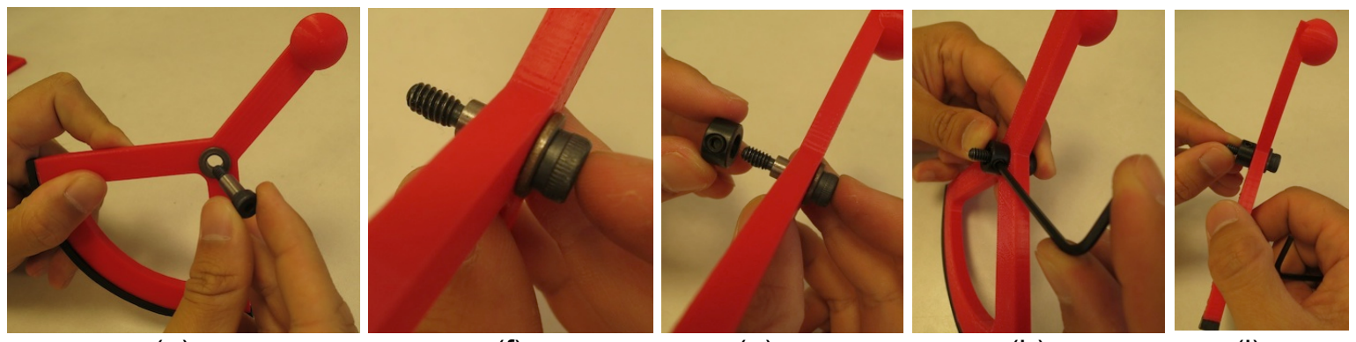
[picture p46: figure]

(e) | (f) | (g) | (h) | (i)
6. Attach the sector pulley to the base. (a, b, c) First, using two ¾” length screws and two wing nuts, attach the 3D-printed height adjustment bar to the back of the upright portion of the 3D-printed base as shown in the first three images below. (d) Then place the shoulder screw (on the sector pulley assembly) into the hole on the height adjustment bar. (e) Use the 1/8" hex key (allen wrench) to screw the shoulder screw into the hole on the height adjustment bar. You will be tapping (creating threads in the plastic of the hole) as you screw it in, so be sure to make the screw go in as straight as possible. You don't need to screw it in very far; just enough to make a secure attachment. You may have to adjust this in conjunction with Step 7 below to ensure a smooth friction drive.

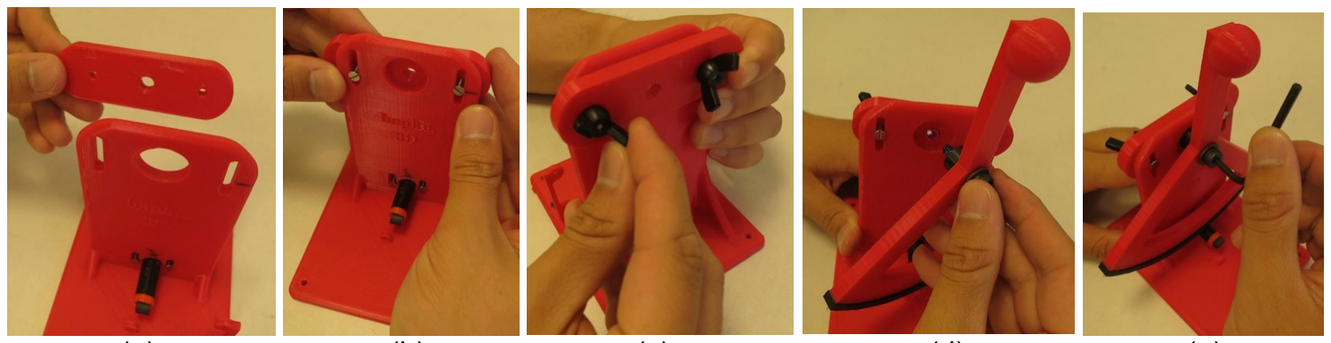
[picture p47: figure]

(a) | (b) | (c) | (d) | (e)

7. Adjust the friction drive. There is a little adjustment to do in order to ensure smooth operation of the Hapkit. In order to adjust the amount of friction between the sector pulley and the drive wheel assembly, loosen the two wing nuts, push the height adjustment bar up or down as needed, such that the neoprene strip is slightly compressed on the drive wheel, but the sector pulley can still swing back and forth without too much force. Then tighten the wing nuts.

Make sure the height has been adjusted so that there is sufficient friction force
between the sector pulley and drive wheel so that turning the drive wheel with your
finger will turn the sector pulley (and vice versa) without slipping.

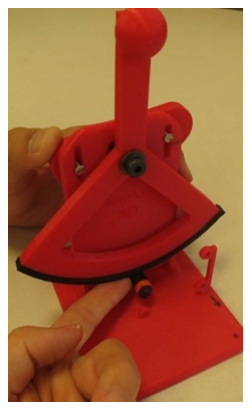
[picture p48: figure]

If your sector pulley feels like it has high friction in some parts of the workspace and low friction in others (i.e., when you move the handle side to side, it is very hard to move in some places and/or loses contact in other places), try loosening the shoulder screw from Step 6. Another possible problem is that your sector pulley arc may not have printed perfectly circular. Air currents around your 3D printer or lack of adhesion to the build surface could be the cause. Consult the 3D printing tips document for solutions; you could alternatively use a laser-cut sector pulley (see 2013 Hapkit design).

8. Solder the magnetoresistive (MR) sensor to the Hapkit board. (a) There is an outline for where the MR sensor should be placed on the Hapkit board. Place the sensor over the outline, such that the side of the sensor with the writing faces outward. (b) Then tilt the sensor up 90 degrees and place the leads all the way into the holes on the Hapkit board. (c) Then fold the sensor down such that the leads are bent and the sensor lies flat against the board (over the outline of the sensor). Do this only once, or the leads may fatigue and fall off. (d, e) Solder each of the three leads of the sensor to the board. (You can find many soldering tutorials online, such as this one: http://www.instructables.com/id/How-to-solder/step4/Soldering-components-onto-a-circuit-board/.)

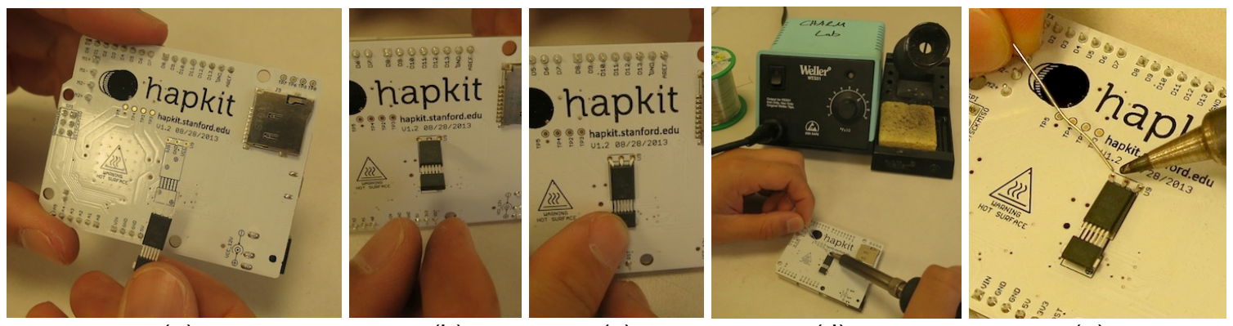
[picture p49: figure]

(a) | (b) | (c) | (d) | (e)
9. Attach the Hapkit board to the 3D-printed base. (a) First lay out the Hapkit board, three 4-40 screws (3/8" long), and three 4-40 nuts as shown below. (b) Use each screw/nut pair in to go through a hold on the Hapkit board and a corresponding hole on the 3D-printed base. This can be tricky, especially if you have big fingers. We suggest pinning the nut to the 3D printed hole with one finger and using the other hand to turn the screw. (c) Tighten with a screwdriver. Verify that the MR sensor is directly facing the magnet mounted on the motor shaft.

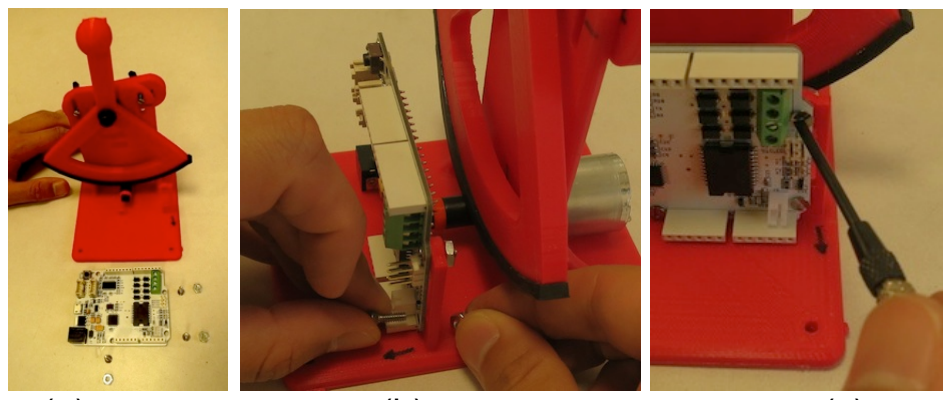
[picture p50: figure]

(a) | (b) | (c)

10. Connect the motor leads. We assume you have already found wires or have a cut-in-half lead with alligator clips to use as connectors between the Hapkit board and the motor. This description assumes you have the alligator clip solution, and that each half of the alligator clip lead now has an alligator clip on one end and stripped (exposed) wire on the other end. (Instructions how to do this are at http://web.media.mit.edu/~leah/LilyPad/01_comp_attach_text2.html#soldering, see steps 3 and 4.)
(a) Use the screwdriver to unscrew the top two terminals on the right side of the Hapkit board. This will open up holes on the right side of the terminal block so you can insert the stripped wire end of the motor leads. (b) Insert a lead into each hole. You may need to twist the leads carefully to get them into the holes. (c) Use the screwdriver to tighten the terminals. (d) Attach the alligator clips on the other ends of the leads to the motor. The lead that is attached to the top terminal screw (labeled M+ on the other side of the Hapkit board) should connect to the lead on the motor with the red dot near it. You can tuck the leads under the small hook on the base to prevent them for getting in the way of the moving sector pulley.

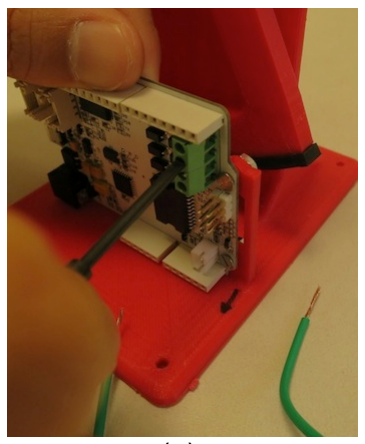
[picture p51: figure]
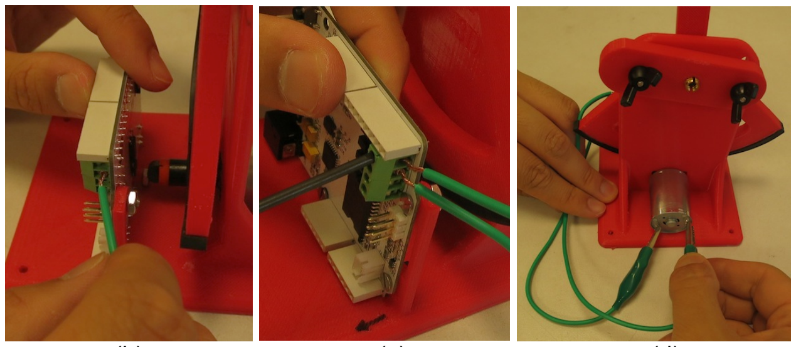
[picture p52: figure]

(a) | (b) | (c) | (d)
11. Final electronic connections. (a) Insert the "micro" end of the USB cable to the connector on the Hapkit board. Hold on to the board with your other hand while you do this. Be very careful during insertion and removal of the USB cable, since (depending on where you get your USB cable), it can be a very tight fit. Warning: It is possible to yank the USB connector off the Hapkit board! (b) Insert the power supply cable (coaxial connector) into the corresponding connector on the Hapkit board.

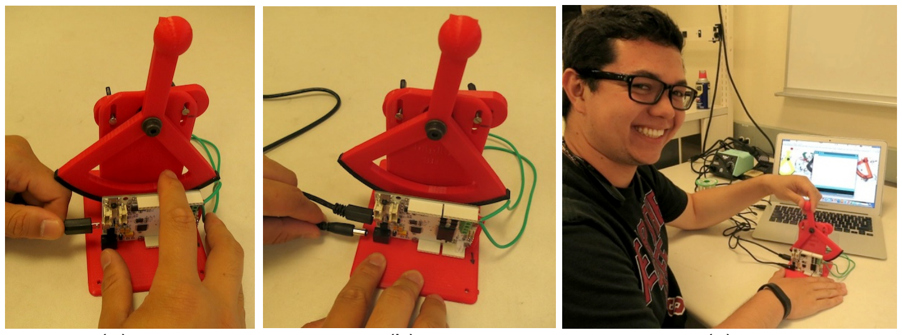
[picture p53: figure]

(a) | (b) | (c)
(c) When you plug the other end of the USB connector into your computer, you should see a green light on your Hapkit board. This tells you that the basic power functions of the Hapkit board are working. (You do not need to plug the power supply into the wall until you want to use the motor, so to avoid unintended motor commands, we suggest you wait to power the motor until you are ready to test it.)

Congratulations – you have successfully assembled your Hapkit. Now you can start programming!

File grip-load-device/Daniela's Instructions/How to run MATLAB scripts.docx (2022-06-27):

Written by: Daniela Herrera

Date: March 2020

To use the MATLAB scripts, the following image shows the folder structure that must be followed in order to run the scripts. As of now, the post processing scripts only process Dynamic and Static Tests. MaxG data must be analyzed individually. This can be easily done in excel by plotting time vs grip force and identifying where the peaks are.

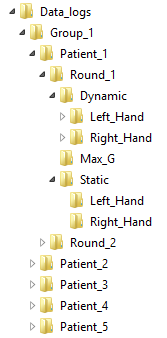
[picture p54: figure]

These folders must be made manually. Future students can create a script that generates these automatically.

Folder conventions

Groups

- Group 1: Control group
- Group 2: MS group

Patients

- Patient_1 through Patient_n: Patient identities are kept safe by assigning a patient with and ID. Use that ID to name their folder in which you will store all their data.

Hand used during testing

- Left_Hand
- Right_Hand

Tests

- Dynamic
  - 0g
  - 450g
- Static
  - LabVIEW will automatically assign a ‘0g’ tag by default. In reality, I only added this tag to differentiate if weight was used for that test. This can be ignored for this test and only applies for dynamic testing.
- MaxG
  - LabVIEW will automatically assign a ‘0g’ tag by default. In reality, I only added this tag to differentiate if weight was used for that test. This can be ignored for this test and only applies for dynamic testing.

Running the scripts

Make sure to download all of the scripts and keep them in the same folder. The main script you will be running is called “postProcessData_FINAL.” The only variables or items you are to change are in lines 10 through 13. See image below.

You don’t need the ‘parent_folder’ variable. I used it for my convenience. You can delete that variable if you wish. For the ‘data_folder’ variable, you must specify the individual test subfolder where your raw data text files are located. Examples of individual tests folders are listed below in bullet points.

- \Round_1\Dynamic\Left_Hand\0g
- \Round_1\Dynamic\Left_Hand\450g
- \Round_1\Dynamic\Right_Hand\0g
- \Round_1\Dynamic\Right_Hand\450g
- \Round_1\Max_G\Left_Hand
- \Round_1\Max_G\Right_Hand
- \Round_1\Static\Left_Hand
- \Round_1\Static\Right_Hand
- \Round_2\Dynamic\Left_Hand\0g
- \Round_2\Dynamic\Left_Hand\450g
- \Round_2\Dynamic\Right_Hand\0g
- \Round_2\Dynamic\Right_Hand\450g
- \Round_2\Max_G\Left_Hand
- \Round_2\Max_G\Right_Hand
- \Round_2\Static\Left_Hand
- \Round_2\Static\Right_Hand

If you look closely at the string assigned for ‘data_folder’, you will see that it follows the folder structure from above. The post processing scripts use this folder structure to identify which MATLAB functions it will use and how to process the data. Lastly, the ‘script_folder’ variable stores the location of your MATLAB scripts.

These scripts will only work if the user does not change the naming convention in the LabVIEW VIs. If changes are made in LabVIEW, the user must reflect those changes in MATLAB.

ICC analysis

For ICC analysis, run the script under the name of “run_ICC_analysis.” To run this script, I used Excel to organize my Matrix of data I analyzed and copied that Matrix directly in variable ‘M’ in line 6. This should be the only variable you modify in this script.

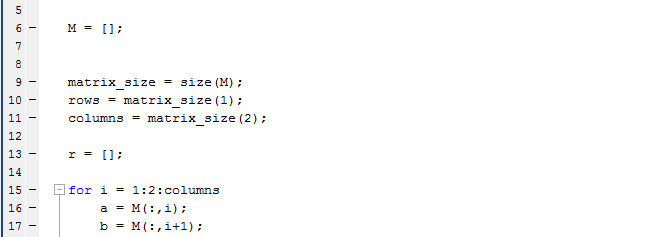
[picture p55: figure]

Feel free to make any modifications or your generate own scripts.

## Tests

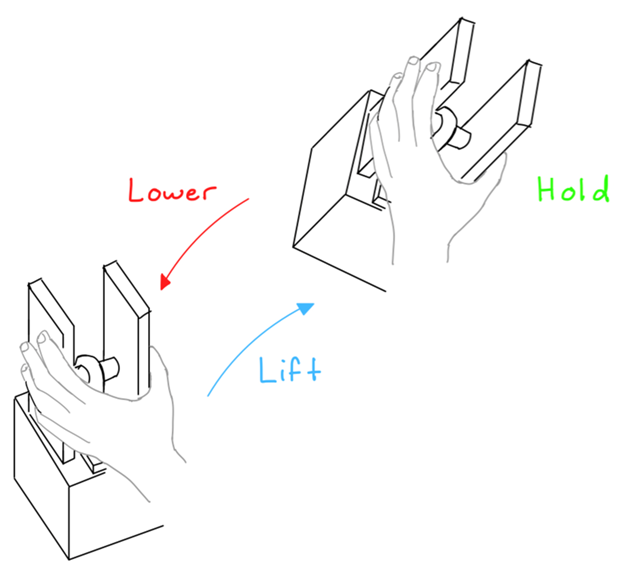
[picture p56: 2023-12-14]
grip-load-device/assets/dynamic-test.png

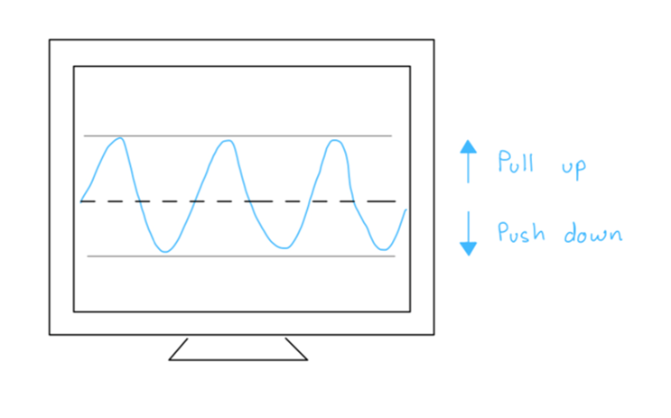
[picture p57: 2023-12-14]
grip-load-device/assets/sine-test.png

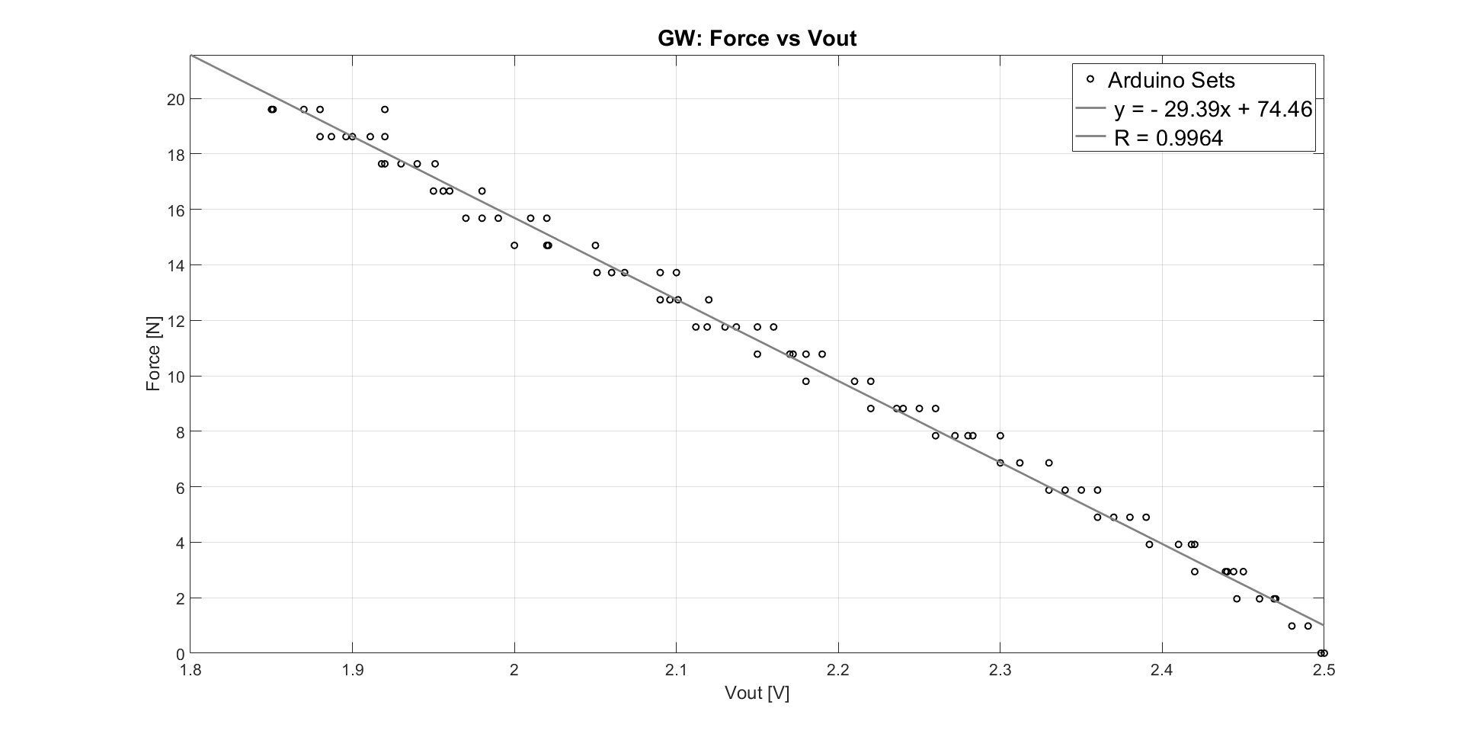
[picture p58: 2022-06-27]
knob-device/assets/important/fsrGW-calibration.png

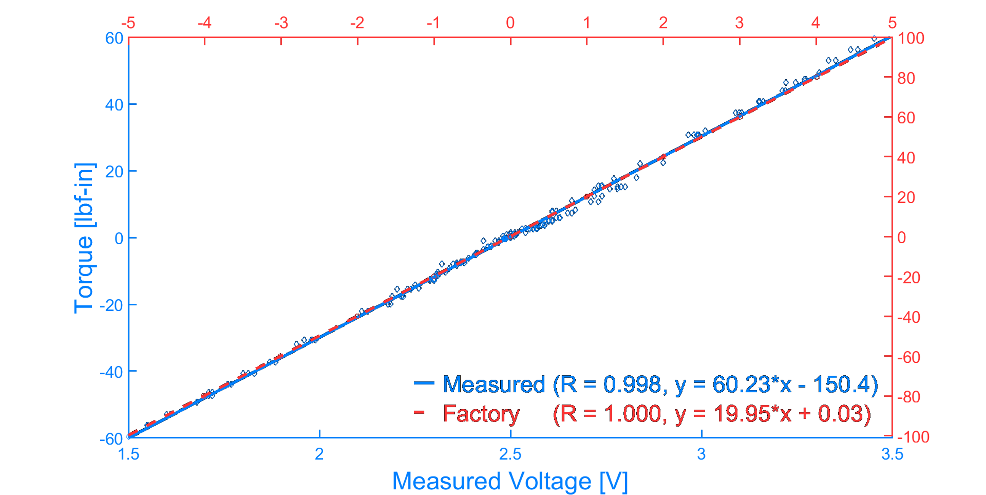
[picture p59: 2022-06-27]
knob-device/assets/important/final-torque-calibration.png

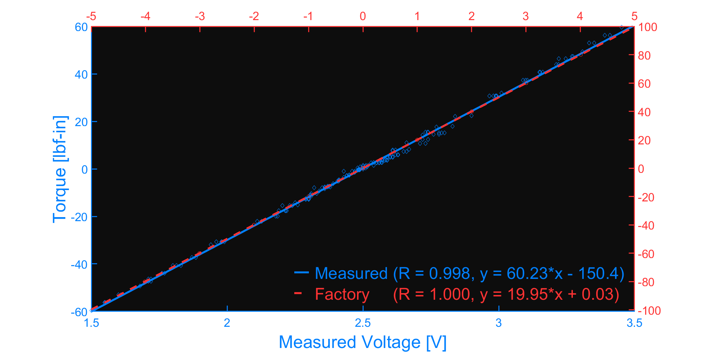
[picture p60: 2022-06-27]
knob-device/assets/important/final-torque-calibration-v2.png

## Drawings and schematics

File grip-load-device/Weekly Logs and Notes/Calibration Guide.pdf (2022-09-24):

### Pushing

↓ ,

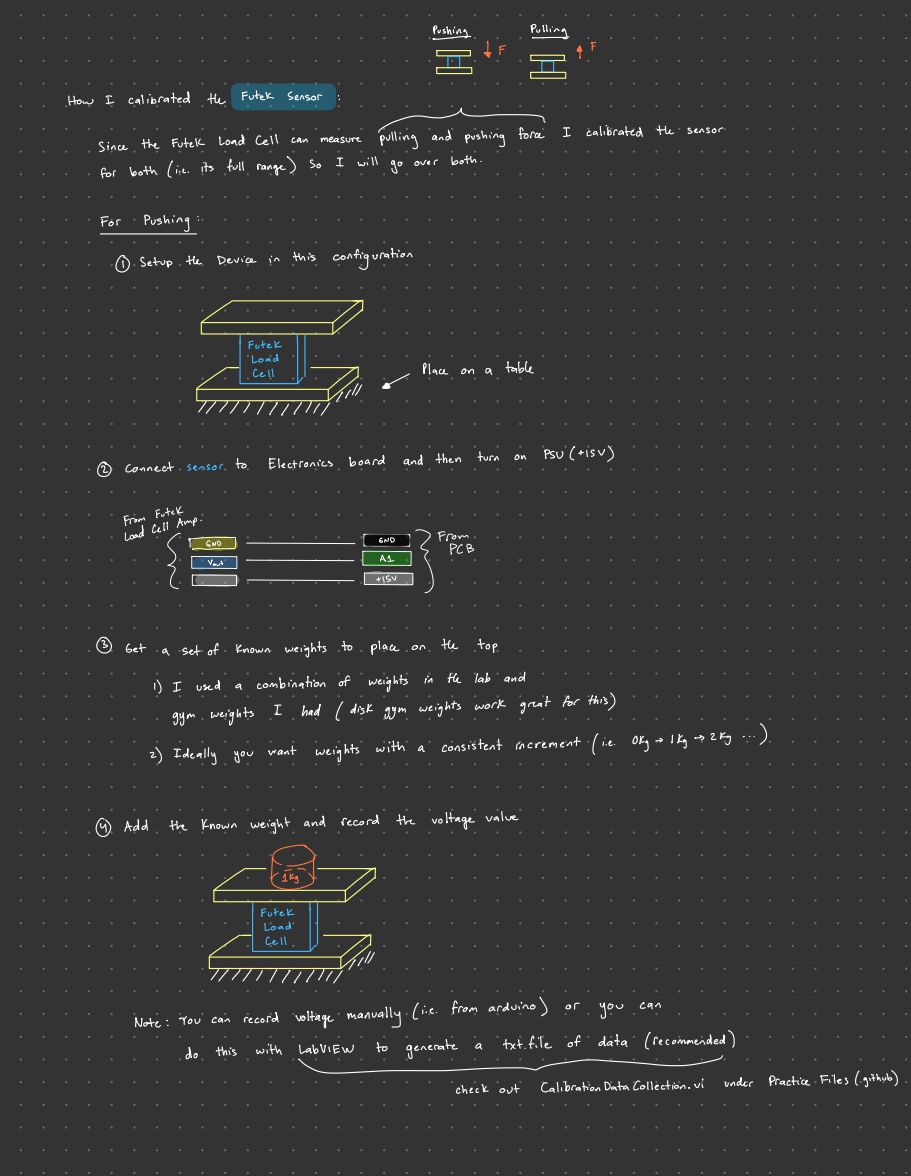
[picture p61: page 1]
Pulling; How I; calibrated; the; Futek; Sensor; Since; Load cell; can; measure; pandÉÉe I; calibrated the; sensor; for; both ( i. e.; its; full range) so; will; go over; both .; For; Pushing :; ① Setup; Device; this; configuration; table; ② Connect; Electronics; board; and then; turn; PSU ( Hsv ); PCB; Vout; + ISV; ③ Get; set of; known; weights to; place on; top; used; combination of; weights in; lab; and; gym weights I; had ( disk gym weights work; great for this); 2) Ideally you; want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

From Futek
Load Cell Amp .

What I | mean | by this | is | you | discretely
add | weight ,

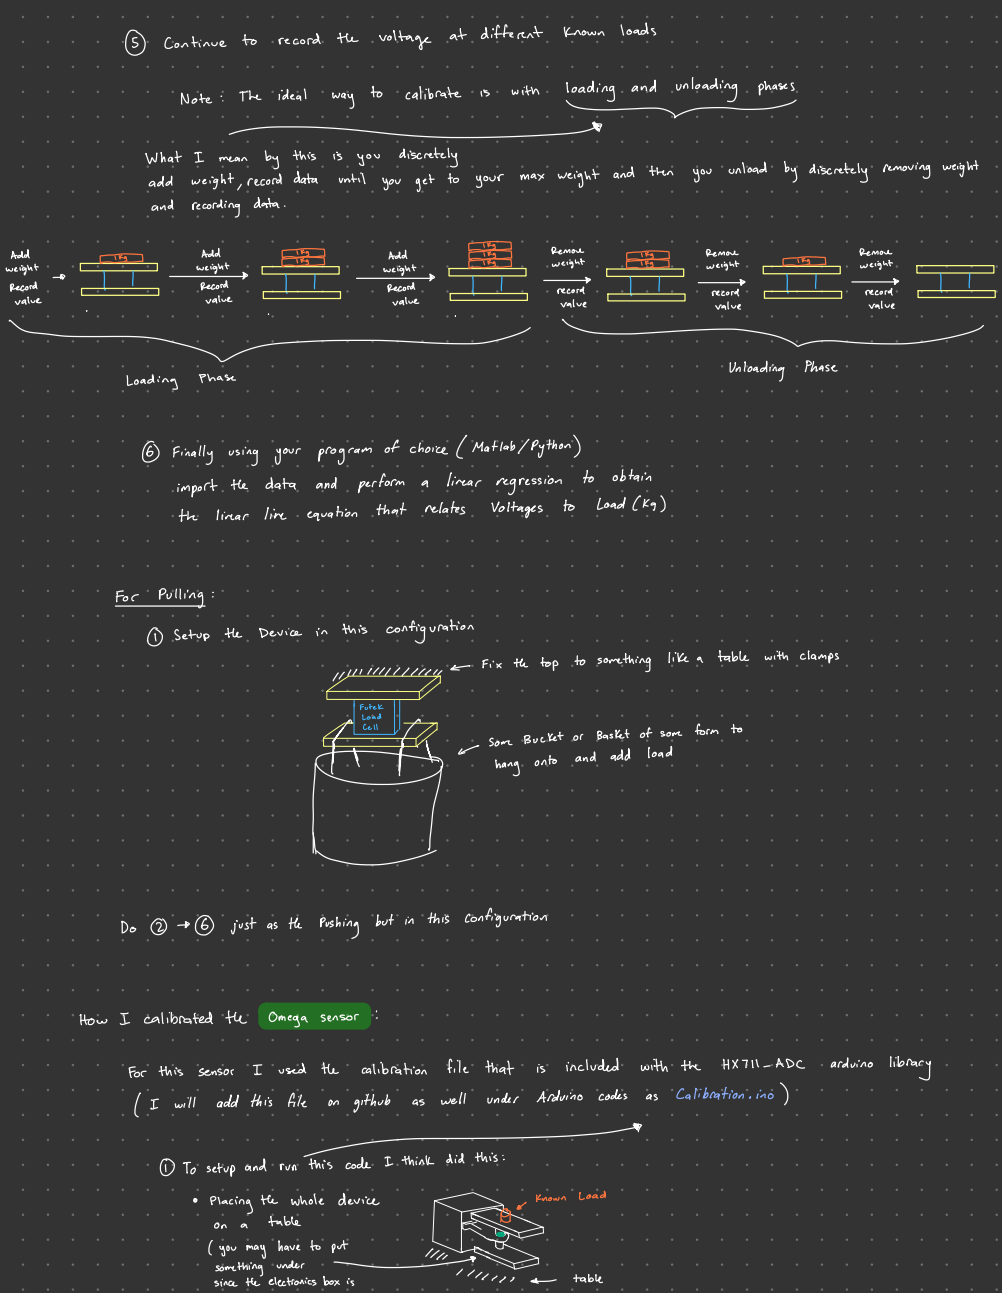
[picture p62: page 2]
⑤ Continue; record; the; voltage at different; known; loads; Note :; The; ideal; way to; calibrate; with; loading and; unloading phases; record data; until; you get to; your max; weight and then; you; unload; by discretely removing weight; and; recording data .; if Add; Add; Renal; weight; \ record; value; valve; Loading; Phase; Unloading Phase; import the; data; perform a; linear regression to; obtain; linear; line; equation; that; relates; Voltages to; Load (Kg ); For; Pulling :; ① Setup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

⑥ Finally using your program of choice ( Matlab /Python )

( you may have to put
something under

I | verified | that | the | readings were | good organist a | scale ( you can | also | measure | the

## readings against the

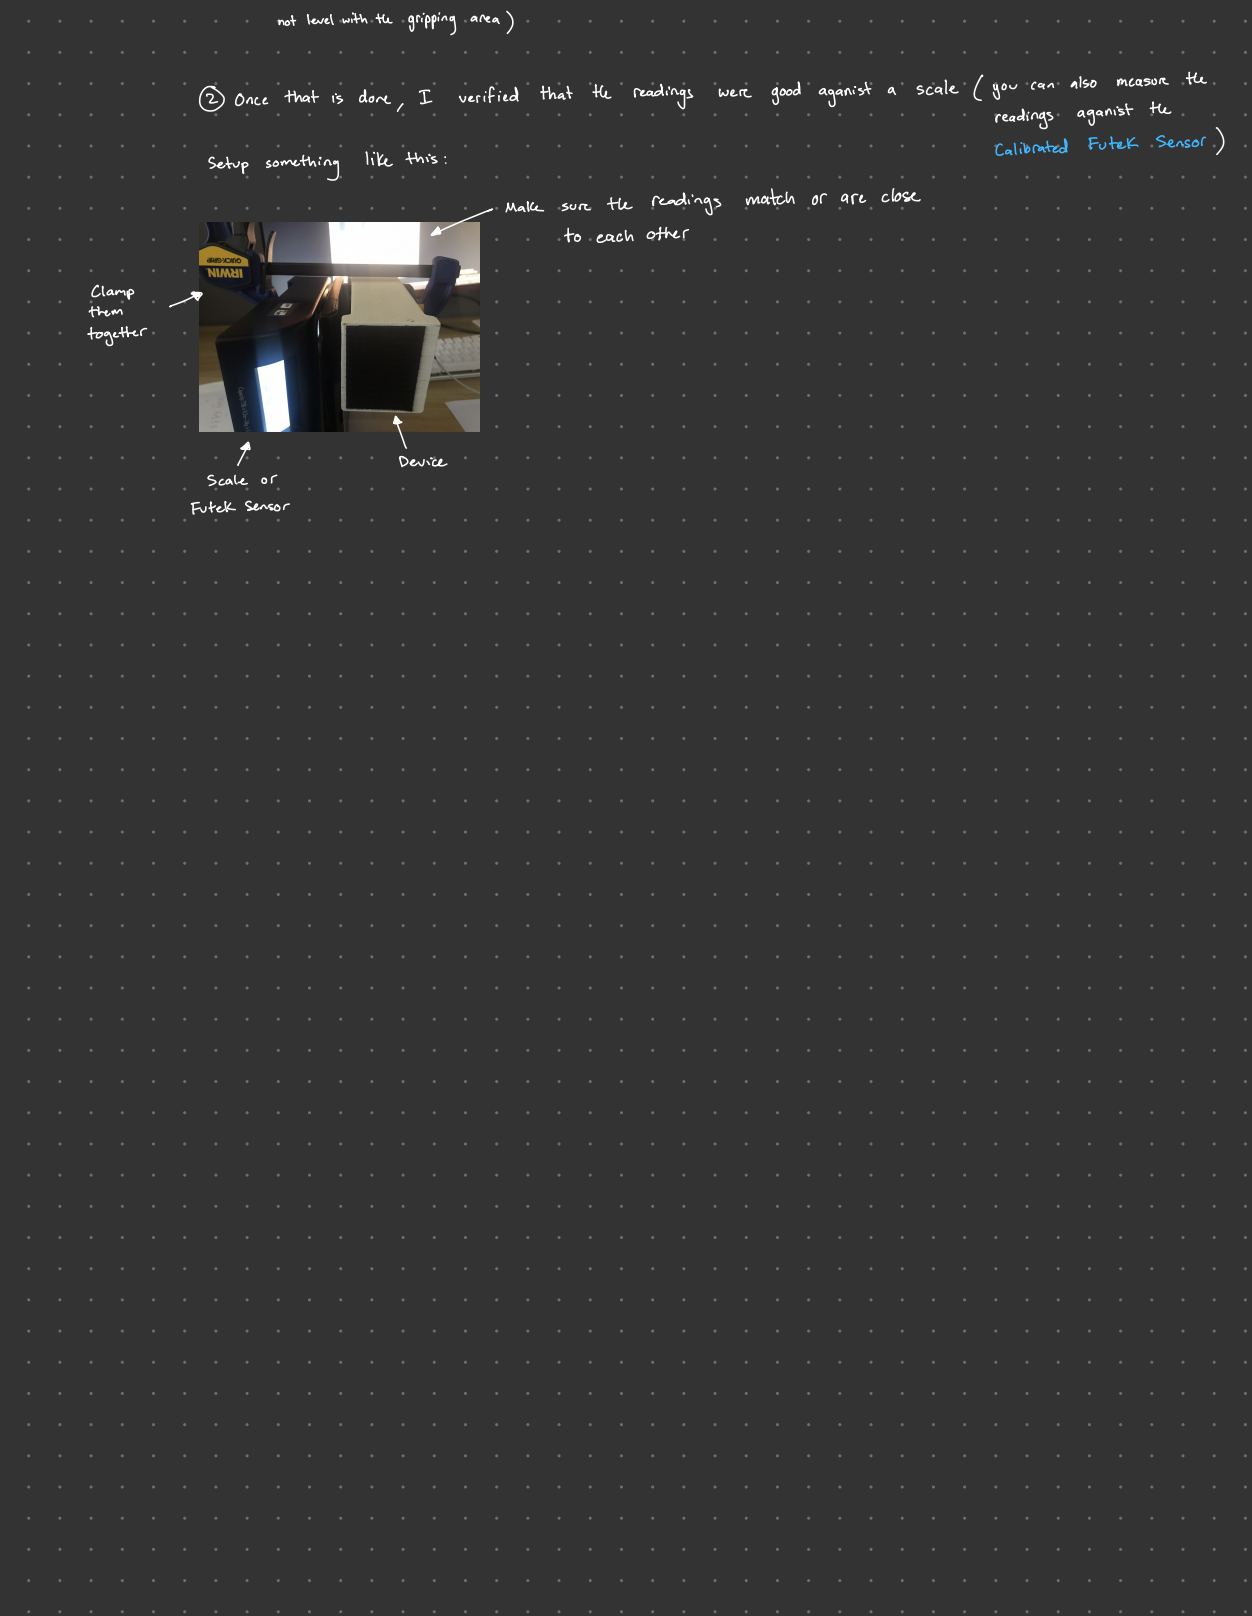
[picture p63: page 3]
not level with the; gripping area ); ② Once; that is; done ,; calibrated Futek; Sensor ); Make; sure; the; readings match or are; close; them; clamp; together; Device; scale or; Futek Sensor

Setup something like this :

to each other

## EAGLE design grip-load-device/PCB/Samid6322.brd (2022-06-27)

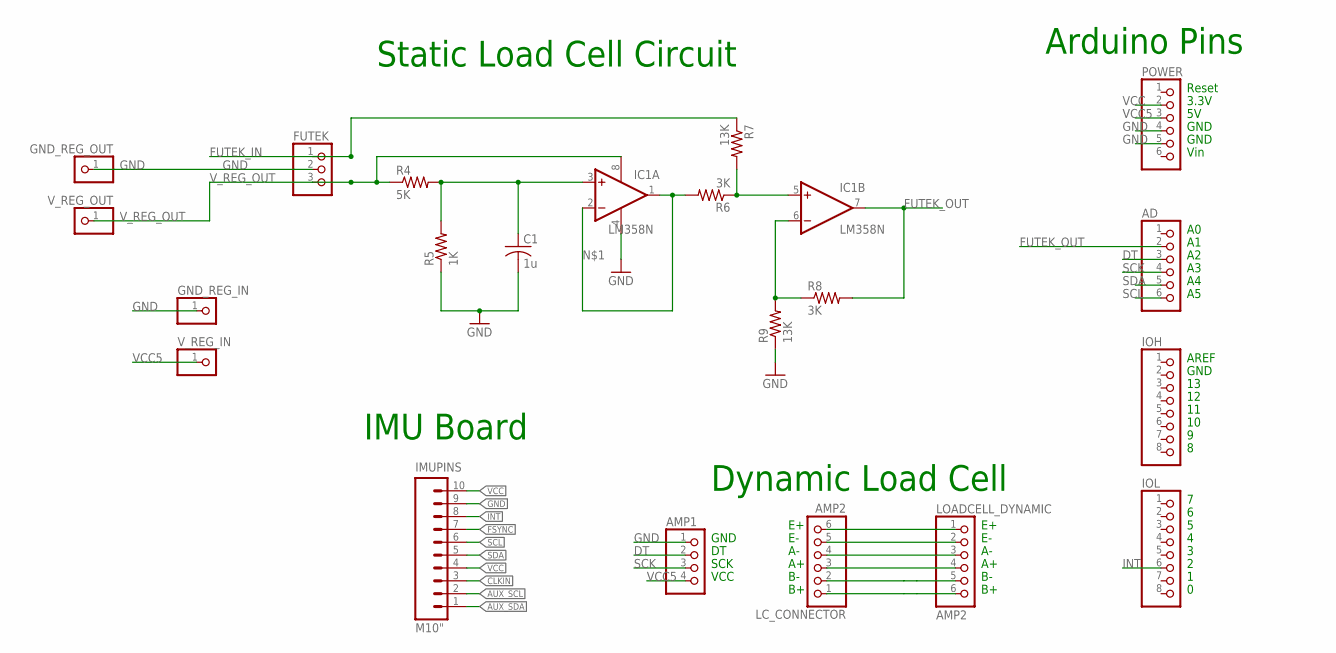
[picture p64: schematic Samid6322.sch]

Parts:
AD: PINHD-1X6; 1X06
AMP1: PINHD-1X4; 1X04
C1: 1u; C025-024X044
FUTEK: PINHD-1X3; 1X03
GND_REG_IN: PINHD-1X1; 1X01
GND_REG_OUT: PINHD-1X1; 1X01
IC1: LM358N; DIL08
IMUPINS: M10"; 1X10
IOH: PINHD-1X8; 1X08
IOL: PINHD-1X8; 1X08
LC_CONNECTOR: AMP2; 1X06
LOADCELL_DYNAMIC: AMP2; 1X06
POWER: PINHD-1X6; 1X06
R4: 5K; 0204/7
R5: 1K; 0204/7
R6, R8: 3K; 0204/7
R7, R9: 13K; 0204/7
V_REG_IN: PINHD-1X1; 1X01
V_REG_OUT: PINHD-1X1; 1X01

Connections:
AUX_SCL: IMUPINS.2
AUX_SDA: IMUPINS.1
CLKIN: IMUPINS.3
DT: AD.3, AMP1.2
FSYNC: IMUPINS.7
FUTEK_IN: FUTEK.1, R7.1
FUTEK_OUT: AD.2, IC1.7 (OUT), R8.2
GND: AMP1.1, C1.2, FUTEK.2, GND_REG_IN.1, GND_REG_OUT.1, IC1.4 (V-), IMUPINS.9, POWER.4, POWER.5, R5.1, R9.1
INT: IMUPINS.8, IOL.6
unnamed: IC1.1 (OUT), IC1.2 (-IN), R6.2
unnamed: LC_CONNECTOR.6, LOADCELL_DYNAMIC.1
unnamed: LC_CONNECTOR.5, LOADCELL_DYNAMIC.2
unnamed: LC_CONNECTOR.4, LOADCELL_DYNAMIC.3
unnamed: LC_CONNECTOR.3, LOADCELL_DYNAMIC.4
unnamed: LC_CONNECTOR.2, LOADCELL_DYNAMIC.5
unnamed: LC_CONNECTOR.1, LOADCELL_DYNAMIC.6
unnamed: IC1.5 (+IN), R6.1, R7.2
unnamed: C1.1, IC1.3 (+IN), R4.2, R5.2
unnamed: IC1.6 (-IN), R8.1, R9.2
SCK: AD.4, AMP1.3
SCL: AD.6, IMUPINS.6
SDA: AD.5, IMUPINS.5
VCC: IMUPINS.4, IMUPINS.10, POWER.2
VCC5: AMP1.4, POWER.3, V_REG_IN.1
V_REG_OUT: FUTEK.3, IC1.8 (V+), R4.1, V_REG_OUT.1

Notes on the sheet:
Reset
3.3V
GND
Vin
AREF
SCK
VCC
IMU Board
Dynamic Load Cell
Arduino Pins
Static Load Cell Circuit

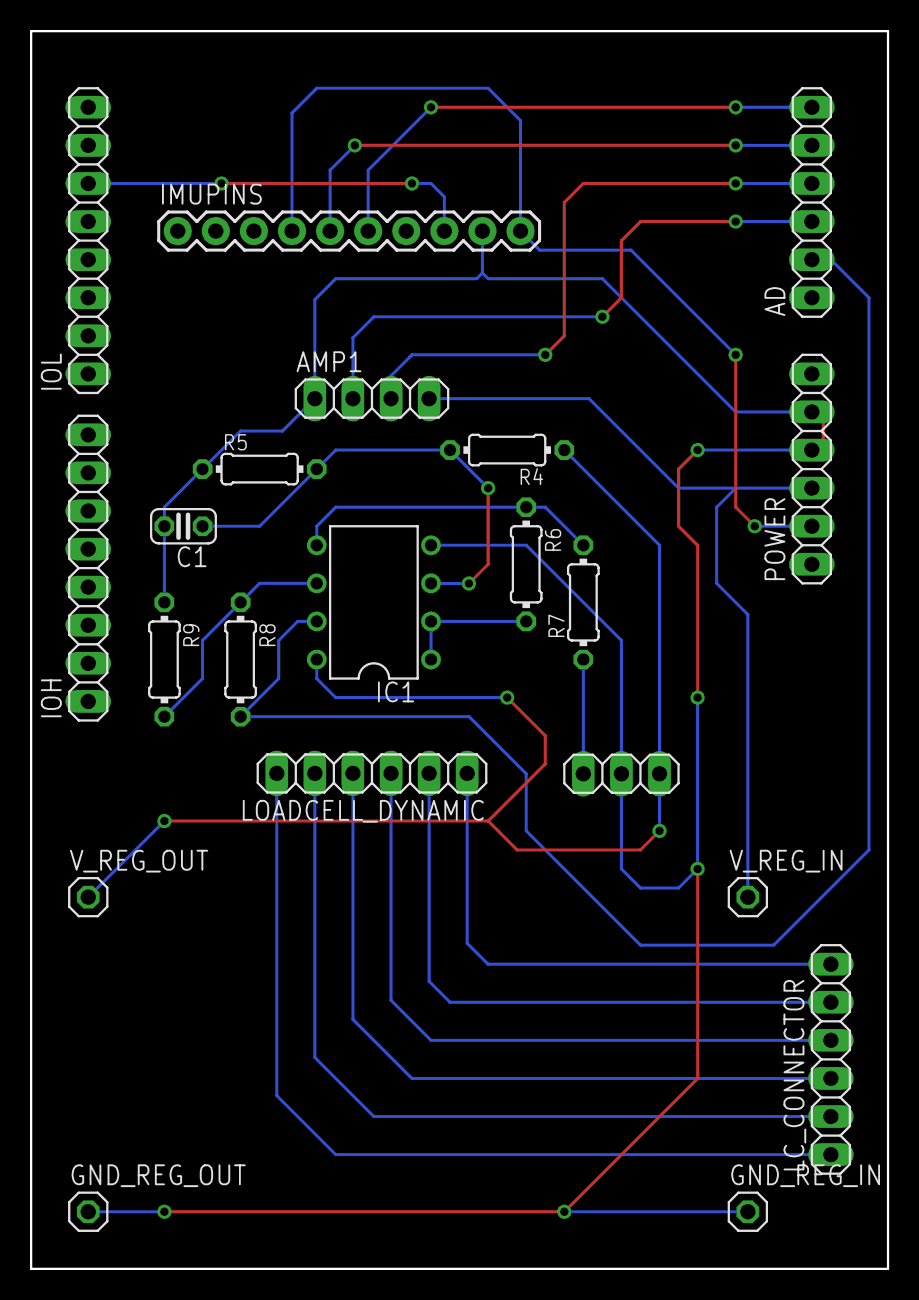
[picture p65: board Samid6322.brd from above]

Board: 2 copper layers, 57.1 x 82.5 mm, 21 parts (0 on the bottom side), 21 nets.

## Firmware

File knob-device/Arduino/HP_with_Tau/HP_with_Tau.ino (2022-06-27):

 //--- Pin Loadout ----//
/*
#define BOpin A0     
#define ROpin A2      
#define GWpin A1  
*/    
#define Tor_pin A2
#define BOpin A3     
#define ROpin A4      
#define GWpin A5
int motorPin = 11;
int dirPin = 13;
int encPin1 = 2;
int encPin2 = 3;


String string = "1003:";
char state;

/**************************************************************************************************************************************************
***************************************************************************************************************************************************
***************************************************************************************************************************************************
*************                                                                                                                        **************
*************     "string" is the input from LabVIEW, and each "byte" from that is represented of the number is as follows:          **************
*************                                                                                                                        **************
*************     string[0] initializes the motor and demonstates the state of the LabVIEW VI (on/off)                               **************
*************       = 0 when enum is set to NO and the program is NOT running.                                                       **************
*************       = 1 when the enum is set to YES and program is running.                                                          **************
*************                                                                                                                        **************
*************     string[1] is to set the test type of the system.                                                                   **************
*************       = 0 for static test.                                                                                             **************
*************       = 1 for dynamic test.                                                                                            

*************     string[2] is for the direction of the test.                                                                        **************
                    = 0 for CW.
*************       = 1 for CCW.
*************                                                                                                                        **************                   
*************     string[3] is for the gain being applied by the motor.                                                              **************
*************       = 0 for low motor gain.                                                                                          **************
*************       = 1 for medium motor gain.                                                                                       **************
*************       = 2 for high motor gain.                                                                                         **************
*************                                                                                                                        **************    
*************      /////////////////////////////////////////////////                                                                 **************
*************     string[4] is for the maximum angle of twist.                                                                       **************
*************       = 0 for 45 degrees.                                                                                              **************
*************       = 1 for 90 degrees.                                                                                              **************
*************                                                                                                                        **************
***************************************************************************************************************************************************
***************************************************************************************************************************************************
**************************************************************************************************************************************************/

//string[n] from above
int Test         = 1;
int Direction    = 2;
int Resistance   = 3;



boolean           stat    = false;
boolean           dyna    = false;
float             beta;                 // (Calculated from Encoder count)
int               motorPwr;             //Power of motor (From LabVIEW)
int               theta   = 0;          //Angle of twist (Calculated from Encoder count)
boolean           dir;
boolean           CW;
boolean           CCW;
boolean           flag_r  = false;
boolean           flag_l  = false;


//--- Encoder Init ---//

volatile long encCount = 0;
int           incomingByte = 0;
volatile int  pin1state;
volatile int  pin2state;
volatile char REGVALS;
void          pin1Change();
void          pin2Change();

boolean       output_enable;



float RO;
float BO;
float GW;
float ROvolt;
float BOvolt;
float GWvolt;
float tor; 
float torV; 

int               x = 20;               //Threshold to be determined later, exaggerated for analysis 

void setup()
{
  Serial.begin(9600);
  Serial.flush();

  pinMode(encPin1,  INPUT);
  pinMode(encPin2,  INPUT);
  pinMode(dirPin,   OUTPUT);
  pinMode(motorPin, OUTPUT);
  pinMode(Tor_pin, INPUT);
  
  pinMode(ROpin,    INPUT);
  pinMode(BOpin,    INPUT);
  pinMode(GWpin,    INPUT);


  attachInterrupt(0, pin1Change, CHANGE);
  attachInterrupt(1, pin2Change, CHANGE);

  pin1state = digitalRead(encPin1);
  pin2state = digitalRead(encPin2);

  output_enable = true;
}

void loop()
{

//----------- Read Values from LabVIEW --------------//
  if (Serial.available() > 0)
  {
    string = "";
  }
  while (Serial.available() > 0)
  {
    state = ((byte)Serial.read());
    if (state == ':')
    {
      break;
    }
    else
    {
      string += state;
    }
    delay(1);
  }


//-- Variable Conversions  ----------------------------------------------------------------------------------------------------------------------------//
//-- Motor Command ------------------------------------------------------------------//
  if (String(string[0]).toInt() == 1)
  {
    analogWrite(motorPin, 0);
  }
  
//-- TEST CASE ------------------------------------------------------------------//
  if (String(string[Test]).toInt() == 0)
  {
    stat = true;
  }
  else if (String(string[Test]).toInt() == 1)
  {
    dyna = true;
  }
  else
  {
    stat = false;
    dyna = false;
  }

 //-- DIRECTION ------------------------------------------------------------------//
  if (String(string[Direction]).toInt() == 0)
  {
     CW  = true;
     CCW  = false;   // made change here
  } 
  else if (String(string[Direction]).toInt() == 1)
  {
     CCW = true;
     CW = false;   // added this line
  }
  
//-- POWER ------------------------------------------------------------------//
  if (String(string[Resistance]).toInt() == 0)
  {
    motorPwr = 85;
  }
  else if (String(string[Resistance]).toInt() == 1)
  {
    motorPwr = 170;
  }
  else if (String(string[Resistance]).toInt() == 2)
  {
    motorPwr = 255;
  }
  
  
 //------------ Read Values from Sensors ----------------------------------------------//
  
  beta = (((long)encCount) * 360.0) / 2000.0;
  theta = beta / 4.1295;                  
  RO = analogRead(ROpin);
  BO = analogRead(BOpin);
  GW = analogRead(GWpin);
  tor = analogRead(Tor_pin);
  ROvolt = RO * (5.0/1023.0);
  BOvolt = BO * (5.0/1023.0);
  GWvolt = GW * (5.0/1023.0);
  torV = tor * (5.0/1023.0);

  
  
 //----- SETTING THE DIRECTION OF THE "MOTOR" ---------------------------------
 if(theta > 0)
 {
   dir = LOW;   
 }
 else if(theta < 0)
 {
   dir = HIGH;
 }
 
 //----- CHANGING FLAG STATES ---------------------------------
 if(theta > x)
 {
   flag_r = true;
 }
 if(theta < -1*x)
 {
   flag_l = true;
 }

 
 //----- CONDITION FOR CW ROTATION (STATIC)---------------------------------
 if(stat == true && CW == true)
 {
   if(theta > x)
   {
     flag_r = true;
   }
   
   if(flag_r == true)
   {
     if(theta > 0)
     {
       analogWrite(motorPin,motorPwr);
       digitalWrite(dirPin,dir);
     }
     else if(theta < 0) //Reset the value of flag
     {
       analogWrite(motorPin,0);
       digitalWrite(dirPin,dir);
       flag_r = false;
     }
   }
 }
 
 //----- CONDITION FOR CCW ROTATION (STATIC)---------------------------------
 if(stat == true && CCW == true)
 {
   if(theta < -1*x)
   {
     flag_l = true;
   }
   if(flag_l == true)
   {
     if(theta < 0)
     {
       analogWrite(motorPin,motorPwr);
       digitalWrite(dirPin,dir);
     }
     else if(theta > 0) //Reset the value of flag
     {
       analogWrite(motorPin,0);
       digitalWrite(dirPin,dir);
       flag_l = false;
     }
   }
 }
 
    //----- CONDITION FOR CW ROTATION (DYNAMIC) ---------------------------------
 if(dyna == true && CW == true)
 {
   if(theta > x)
   {
     flag_r = true;
   }
   
   if(flag_r == true)
   {
     if(theta > 0)
     {
       analogWrite(motorPin,motorPwr);
       digitalWrite(dirPin,dir);
     }
     else if(theta < 0) //Reset the value of flag
     {
       analogWrite(motorPin,0);
       digitalWrite(dirPin,dir);
       flag_r = false;
     }
   }
 }
 
 //----- CONDITION FOR CCW ROTATION (DYNAMIC)---------------------------------
 if(dyna == true && CCW == true)
 {
   if(theta < -1*x)
   {
     flag_l = true;
   }
   if(flag_l == true)
   {
     if(theta < 0)
     {
       analogWrite(motorPin,motorPwr);
       digitalWrite(dirPin,dir);
     }
     else if(theta > 0) //Reset the value of flag
     {
       analogWrite(motorPin,0);
       digitalWrite(dirPin,dir);
       flag_l = false;
     }
   }
 }     

//----------- Send Values to LabVIEW ----------------//
  Serial.print(ROvolt);  
  Serial.print(",");
  Serial.print(GWvolt);
  Serial.print(",");
  Serial.print(BOvolt);
  Serial.print(","); 
  Serial.print(theta);
  Serial.print(",");
  Serial.println(torV);
  
  
}

// Encoder count code //
void pin1Change() {
  REGVALS = PIND;
  pin1state = REGVALS & B00000100;
  pin2state = REGVALS & B00001000;

  if (pin1state == B00000100) {
    if (pin2state == B00000000) {
      encCount++;
    }
    else {
      encCount--;
    }
  }
  else {
    if (pin2state == B00001000) {
      encCount++;
    }
    else {
      encCount--;
    }
  }
}


void pin2Change() {
  REGVALS = PIND;
  pin1state = REGVALS & B00000100;
  pin2state = REGVALS & B00001000;

  if (pin1state == B00000100) {
    if (pin2state != B00000000) {
      encCount++;
    }
    else {
      encCount--;
    }
  }
  else {
    if (pin2state != B00001000) {
      encCount++;
    }
    else {
      encCount--;
    }
  }
}

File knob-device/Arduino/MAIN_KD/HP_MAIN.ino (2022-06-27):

 //--- Pin Loadout ----//

#define TORpin A2 // Vout from torque sensor circuit   
#define F1pin A3  //  for b2: M   red wire
#define F2pin A4  //   for b2: RO  white wire
#define F3pin A5  //   for b2: BO  green wire


#define motorPin 11
#define dirPin 13
#define encPin1 2
#define encPin2 3


String string = "1030:";
char state;

/**************************************************************************************************************************************************
***************************************************************************************************************************************************
***************************************************************************************************************************************************
*************                                                                                                                        **************
*************     "string" is the input from LabVIEW, and each "byte" from that is represented of the number is as follows:          **************
*************                                                                                                                        **************
*************                                                                                                                        **************
*************     string[0] is to set the test type of the system.                                                                   **************
*************       = 0 for static test.                                                                                             **************
*************       = 1 for dynamic test.                                                                                            

*************     string[1] is for the direction of the test.                                                                        **************
                    = 0 for CW.
*************       = 1 for CCW.
*************                                                                                                                        **************                   
*************     string[2] is for the gain being applied by the motor.                                                              **************
*************       = 0 for low motor gain.                                                                                          **************
*************       = 1 for medium motor gain.                                                                                       **************
*************       = 2 for high motor gain.                                                                                         **************
*************                                                                                                                        **************    
*************      /////////////////////////////////////////////////                                                                 **************
*************     string[3] is to start motor.                                                                                       **************
*************       = 0 for 0 motor gain degrees.                                                                                    **************
*************       = 1 for the motor gain set in string[2].                                                                         **************
*************                                                                                                                        **************
***************************************************************************************************************************************************
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

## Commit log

2022-06-27 arduino code
2022-06-27 final solidworks files
    [FinalcollarAssembly.SLDASM, LCFD.SLDPRT, bottom_collar2.SLDPRT, plate_attachment.SLDPRT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]
2022-06-27 pcb files, datasheets, and references
    [Copy of CSG110GainSettings.xls, Samid6322.brd, Samid6322.sch]
2022-06-27 old solidworks files
    [Assem_Plates.SLDASM, GFAttachmentOval.SLDPRT, GFhexAttachment.SLDPRT, LC_attachmentV2.SLDPRT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]
2022-06-27 BOM etc.
    [Bill of Materials GLD.xlsx]
2022-06-27 sw files
    [Brace.SLDASM, Hinge_test.SLDPRT, Palm.SLDPRT, Wrist.SLDPRT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]
2022-06-27 3d print files, and papers
    [PalmLarge.STL, PalmO.STL, hinge_test.STL]
2022-06-27 hapkit stuff
    [110923_Amax26_GB_6W_KL_1WE.stp.SLDPRT, Base.SLDPRT, Base.STL, DriveWheel.SLDPRT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]
2022-09-24 Calibration for omega (GF) sensor
2023-12-14 clean up
    [110923_Amax26_GB_6W_KL_1WE.stp.SLDPRT, Assem_Plates.SLDASM, Base.SLDPRT, Base.STL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]
